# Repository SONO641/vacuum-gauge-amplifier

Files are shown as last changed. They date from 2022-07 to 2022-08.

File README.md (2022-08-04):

# amplifier board for thermocouple vacuum gauge

### Description of the control board for vacuum thermocouple gauge.



I found <a href="http://www.belljar.net/tcgauge.htm">
this tutorial</a>  about the operating principle of thermocouple vacuum gauges. I designed the board below based on the article. 

A thermocouple vacuum gauge works by heating a filament at a constant current. The filament’s temperature is higher at a lower pressure because it only loses heat by radiation. The temperature is lower at higher pressure because of the heat loss via the convection of gas in addition to radiation. A thermocouple reads the filament’s temperature and produces a DC signal a function of the temperature difference from the end of the wire. For the gauge I used (KJL-1518) maximum thermocouple voltage is 10mV. I used an instrument amplifier (INA128) to amplify the mV signal by a factor of 330.

The circuit has two parts. One is to supply current to the filament. I used LM317 to limit the current to 16mA. The 5V DC supply for the filament has to be isolated, otherwise thermocouple won't work. I used another DC-DC converter for the instrument amplifier to supply ±9V for INA128. Using this setup, a few mtorr pressure gives 3.7V and 100mtorr 1V between SIG and REF pins. Calibrate the gauve following the artible above.  

A commercial thermocouple gauge controller costs about USD 700 with a display and serial output. Parts for the amplifier board was about USD 25. I use ADS1115 to measure analog signals, and a Raspberry Pi to communicate and log the pressure to a server. Total cost was under USD 100. 

Connect filament +/- to gauge pins 1 and 7, and TC gauge +/- to pin 5/3 of the thermocouple gauge. Apply 5V DC voltage between VIN and GND. Measure voltage between SIG and REF. Applying 5V to enable (EN) to apply current to the filament; pulling EN pin down will shut off the filament current. It may take a few min to filament to heat up, and give steady vacuum readings.

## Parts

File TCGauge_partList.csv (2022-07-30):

Digi-key Part Number | Description | Unit Price
102-PEP1-S5-D9-M-ND | DC DC CONVERTER +/-9V 1W | 4.83
102-PEP1-S5-S5-M-ND | DC DC CONVERTER 5V 1W | 4.66
LM317MADTRKGOSCT-ND | IC REG LINEAR POS ADJ 500MA DPAK | 0.96
RMCF0805FT100KCT-ND | RES 100K OHM 1% 1/8W 0805 | 0.027
311-75.0CRCT-ND | RES SMD 75 OHM 1% 1/8W 0805 | 0.042
P110DACT-ND | RES 110 OHM 0.1% 1/8W 0805 | 0.31
311-10.0KCRCT-ND | RES SMD 10K OHM 1% 1/8W 0805 | 0.042
311-3427-1-ND | CAP CER 1UF 16V X5R 0805 | 0.13
478-10836-1-ND | CAP CER 0.1UF 50V X7R 0805 | 0.076
296-26057-1-ND | Texas Instruments IC INST AMP 1 CIRCUIT 8SOIC | 9.36
732-4980-1-ND | LED GREEN CLEAR 0603 SMD | 0.15
TSM240N03CX RFG | MOSFET N-CHANNEL 30V 6.5A SOT23 | 0.94

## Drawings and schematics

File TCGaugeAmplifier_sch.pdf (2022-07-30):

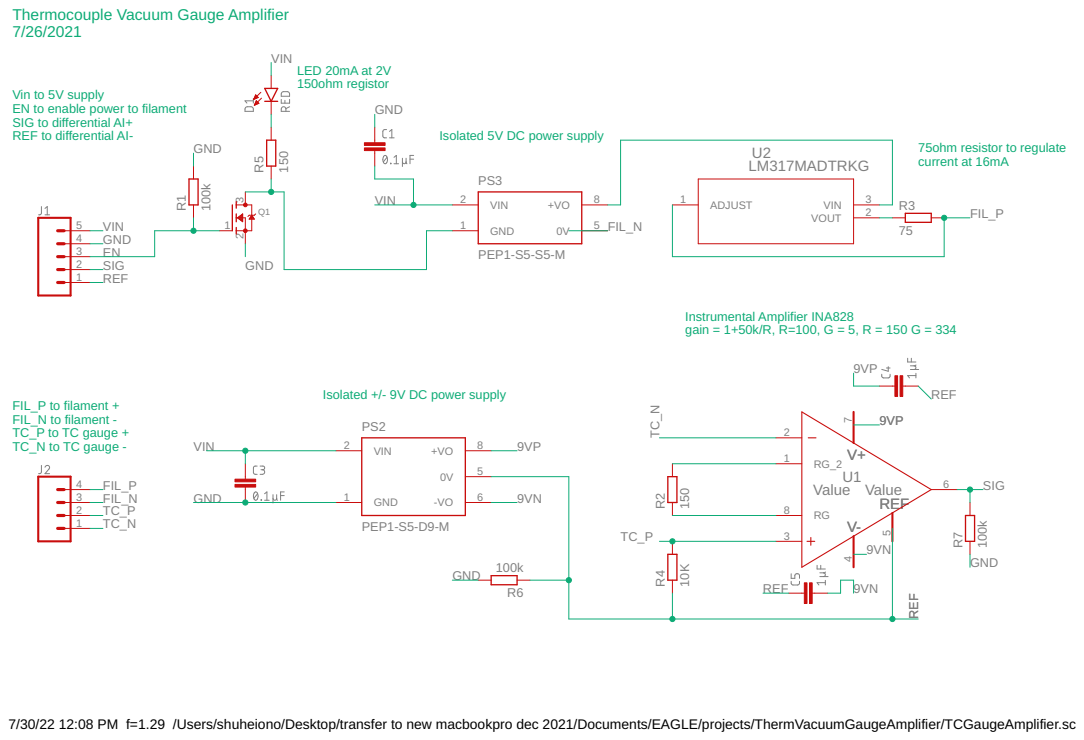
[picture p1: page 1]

Thermocouple Vacuum Gauge Amplifier

Vin to 5V supply
EN to enable power to filament
SIG to differential AI+
REF to differential AI-

Isolated 5V DC power supply

Isolated +/- 9V DC power supply

FIL_P to filament +
FIL_N to filament - TC_P to TC gauge +

7/30/22 12:08 PM f=1.29 /Users/shuheiono/Desktop/transfer to new macbookpro dec 2021/Documents/EAGLE/projects/ThermVacuumGaugeAmplifier/TCGaugeAmplifier.sch (Sheet: 1/1)

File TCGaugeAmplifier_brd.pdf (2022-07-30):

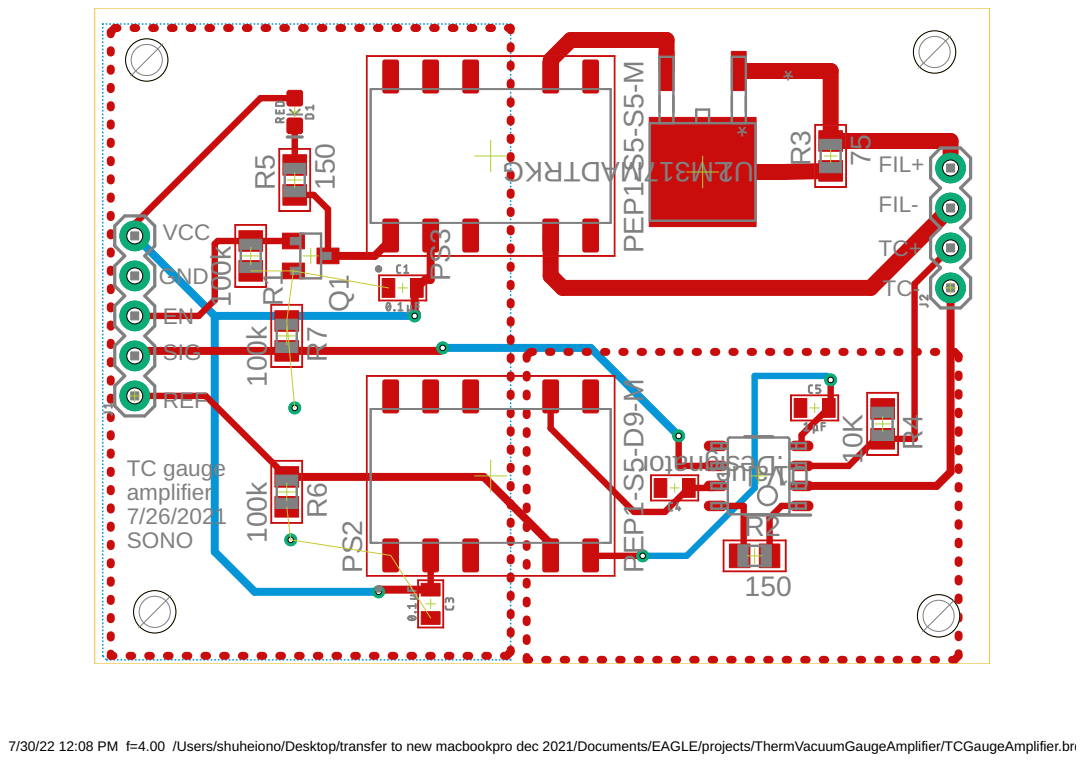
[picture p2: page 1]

7/30/22 12:08 PM f=4.00 /Users/shuheiono/Desktop/transfer to new macbookpro dec 2021/Documents/EAGLE/projects/ThermVacuumGaugeAmplifier/TCGaugeAmplifier.brd

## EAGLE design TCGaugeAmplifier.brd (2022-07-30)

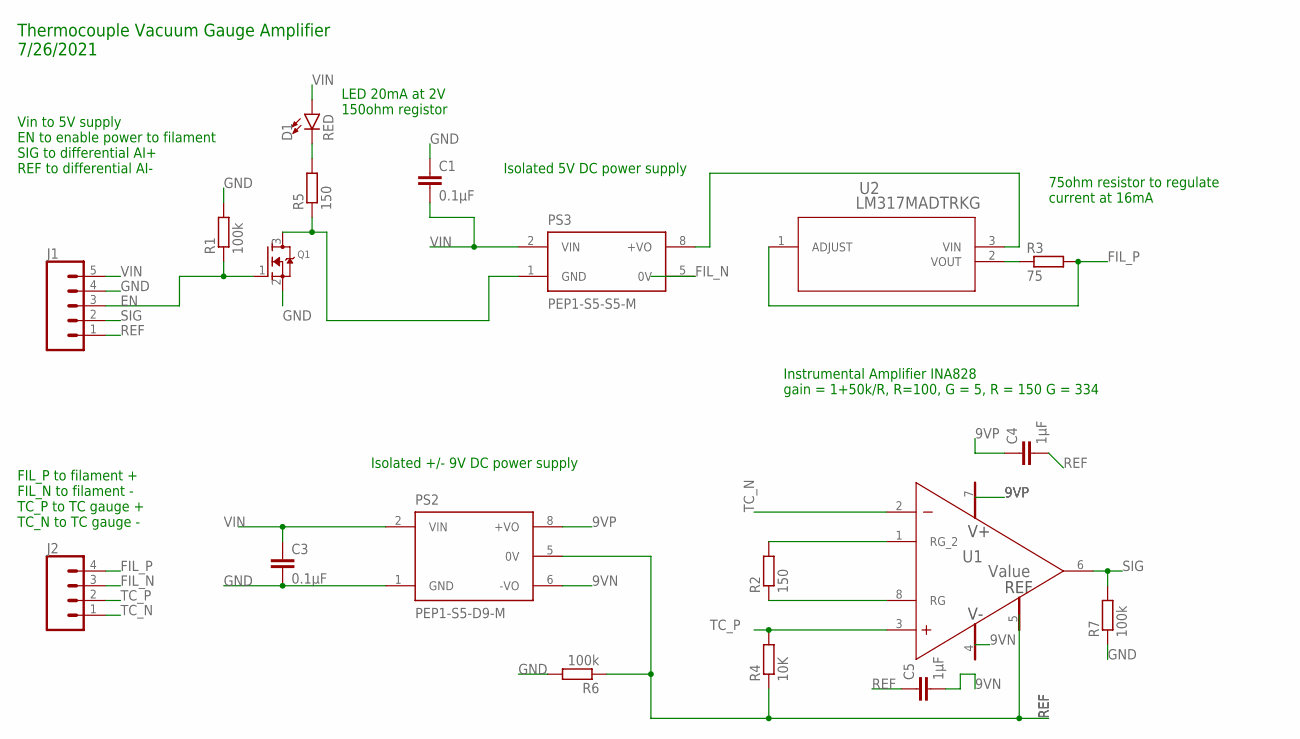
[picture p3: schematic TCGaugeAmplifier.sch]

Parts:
C1, C3: 0.1µF; 0805
C4, C5: 1µF; 0805
D1: RED; LED-0603
J1: CONN_05; 1X05
J2: CONN_04; 1X04
PS2: PEP1-S5-D9-M; CONV_PEP1-S5-D9-M
PS3: PEP1-S5-S5-M; CONV_PEP1-S5-S5-M
Q1: MOSFET-NREFLOW; SOT23
R1, R6, R7: 100k; R0805
R2, R5: 150; R0805
R3: 75; R0805
R4: 10K; R0805
U1: Value; D0008A_N
U2: LM317MADTRKG; DPAK-3_ONS

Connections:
9VN: C5.2, PS2.6 (-VO), U1.4 (V-)
9VP: C4.1, PS2.8 (+VO), U1.7 (V+)
EN: J1.3, Q1.1 (G), R1.1
FIL_N: J2.3, PS3.5 (0V)
FIL_P: J2.4, R3.2, U2.1 (ADJUST)
GND: C1.1, C3.2, J1.4, PS2.1 (GND), Q1.2 (S), R1.2, R6.2, R7.1
unnamed: R2.2, U1.1 (RG_2)
unnamed: R2.1, U1.8 (RG)
unnamed: PS3.8 (+VO), U2.3 (VIN)
unnamed: R3.1, U2.2 (VOUT)
unnamed: D1.C, R5.2
unnamed: PS3.1 (GND), Q1.3 (D), R5.1
REF: C4.2, C5.1, J1.1, PS2.5 (0V), R4.1, R6.1, U1.5 (REF)
SIG: J1.2, R7.2, U1.6 (OUT)
TC_N: J2.1, U1.2 (IN-)
TC_P: J2.2, R4.2, U1.3 (IN+)
VIN: C1.2, C3.1, D1.A, J1.5, PS2.2 (VIN), PS3.2 (VIN)

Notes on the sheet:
Vin to 5V supply EN to enable power to filament SIG to differential AI+ REF to differential AI-
FIL_P to filament + FIL_N to filament - TC_P to TC gauge + TC_N to TC gauge -
Isolated 5V DC power supply
Isolated +/- 9V DC power supply
LED 20mA at 2V 150ohm registor
75ohm resistor to regulate current at 16mA
Instrumental Amplifier INA828 gain = 1+50k/R, R=100, G = 5, R = 150 G = 334
Thermocouple Vacuum Gauge Amplifier 7/26/2021

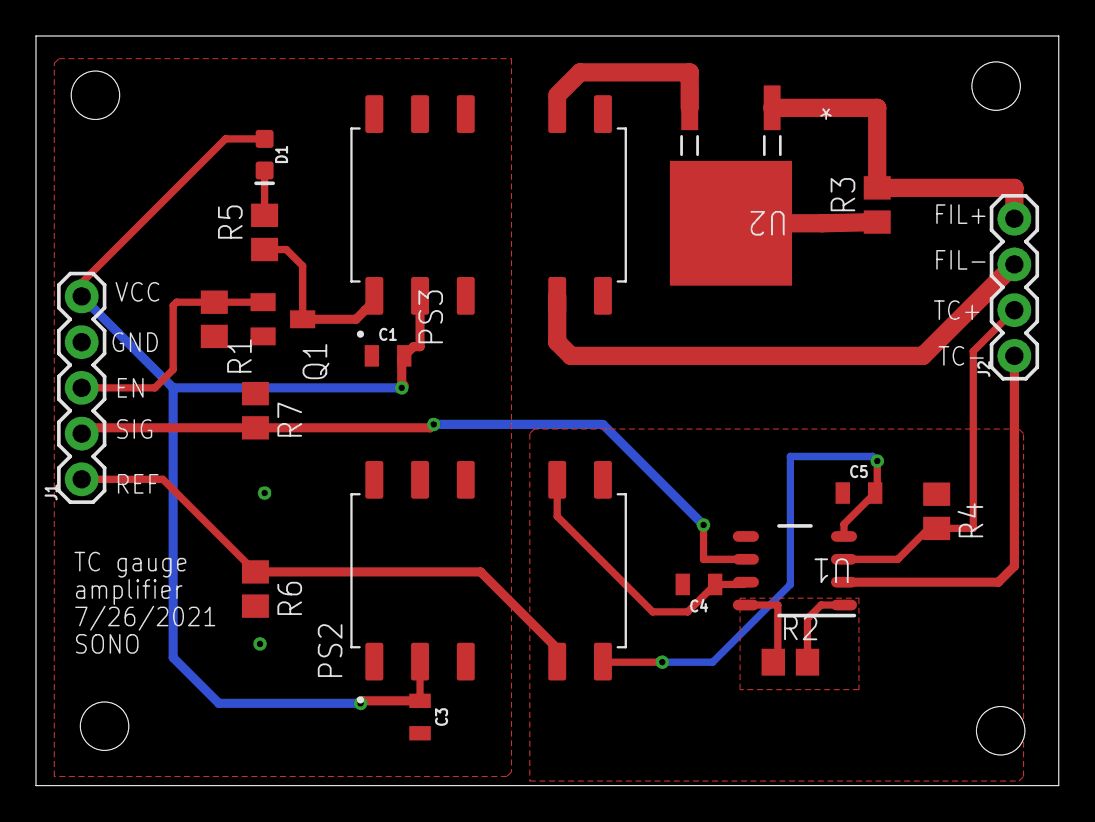
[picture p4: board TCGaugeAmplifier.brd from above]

Board: 2 copper layers, 56.8 x 41.6 mm, 19 parts (0 on the bottom side), 17 nets.

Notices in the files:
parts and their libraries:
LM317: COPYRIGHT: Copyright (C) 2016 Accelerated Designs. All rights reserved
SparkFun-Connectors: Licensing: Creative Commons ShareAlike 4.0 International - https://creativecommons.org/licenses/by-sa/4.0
